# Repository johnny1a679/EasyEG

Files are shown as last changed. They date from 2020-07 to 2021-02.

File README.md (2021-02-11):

# EasyEG

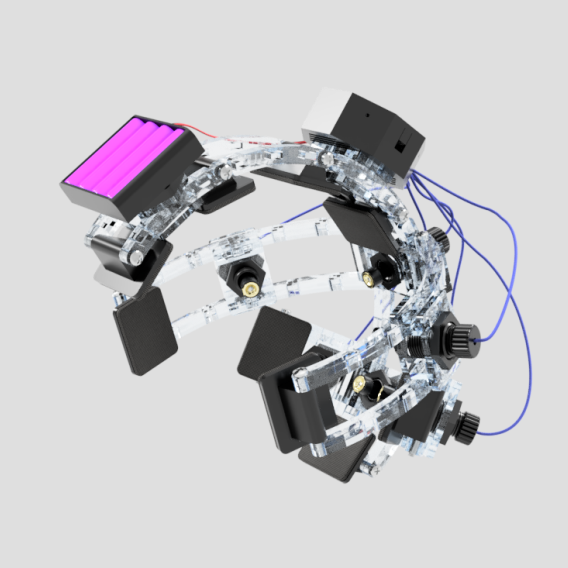
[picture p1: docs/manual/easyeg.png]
EasyEG


Brain-Computer Interfaces (BCIs) are progressively adopted by the consumer market, making them available for a variety of use-cases. However, off-the-shelf BCIs are limited in their adjustments towards individual head shapes, evaluation of scalp-electrode contact, and extension through additional sensors. This work presents __EasyEG__, a BCI headset that is adaptable to individual head shapes and offers adjustable electrode-scalp contact to improve measuring quality. __EasyEG__ consists of 3D-printed and low-cost components that can be extended by additional sensing hardware, hence expanding the application domain of current BCIs.

## Construction Manual

The following steps explain how to assemble your own __EasyEG__.
You can produce the parts either by [3D-printing](3d-printer_only) or by combining [laser cutting and 3D-printing](lasercutter_and_3d-printer) if you have access to a laser cutter and an M4 tap.

### List of Materials

#### Produced Parts With 3D-Printing Only

- 9 x [Head Plate](3d-printer_only/rails/head-plate.stl)

- [Front Rail](3d-printer_only/rails/rail_front.stl) and [Front Rail Threaded](3d-printer_only/rails/rail_front_threaded.stl)
- 2 x [Top Rail](3d-printer_only/rails/rail_top.stl) and 2 x [Top Rail Threaded](3d-printer_only/rails/rail_top_threaded.stl)
- [Long Rail](3d-printer_only/rails/rail_long.stl) and [Long Rail Threaded](3d-printer_only/rails/rail_long_threaded.stl)
- 2 x [Long Side Rail](3d-printer_only/rails/rail_side_long.stl) and 2 x [Long Side Rail Threaded](3d-printer_only/rails/rail_side_long_threaded.stl)
- 2 x [Short Side Rail](3d-printer_only/rails/rail_side_short.stl) and 2 x [Short Side Rail Threaded](3d-printer_only/rails/rail_side_short_threaded.stl)

- 2 x [Main Clamp Top](3d-printer_only/clamps/main_clamp_top.stl) and 2 x [Main Clamp Bottom](3d-printer_only/clamps/main_clamp_bottom.stl)
- 1 x [Clamp Top](3d-printer_only/clamps/clamp_top.stl) per electrode on the sides + 1 for the BCI Case
- 1 x [Clamp Bottom](3d-printer_only/clamps/clamp_bottom.stl) per electrode on the sides
- 2 x [Accessory Clamp Bottom](3d-printer_only/clamps/accessory_clamp_bottom.stl)
- 1 x [Battery Clamp Top](3d-printer_only/clamps/battery_clamp_top.stl)
- 2 x [Screw Sleeve](3d-printer_only/clamps/electrode_screwsleeve.stl)

- one of each of the following for every electrode:
  - [Electrode Nut](3d-printer_only/electrode_mount/electrode_nut.stl)
  - [Electrode Mount](3d-printer_only/electrode_mount/electrode_mount.stl)
  - [Electrode Inner Slider](3d-printer_only/electrode_mount/electrode_inner_slider.stl)
  - [Electrode Outer Screw Part 1](3d-printer_only/electrode_mount/electrode_outer_screw_part1.stl)
  - [Electrode Outer Screw Part 2](3d-printer_only/electrode_mount/electrode_outer_screw_part2.stl)

- BCI-Case [Top](3d-printer_only/bci-case_top.stl) and [Bottom](3d-printer_only/bci-case_bottom.stl)

#### Produced Parts With Laser Cutting and 3D-Printing

- Laser cut the following sheets from 4mm acrylic:
  - [Rails](lasercutter_and_3d-printer/lasercut/easyeg_lasercut_rails.svg)
  - [Clamps](lasercutter_and_3d-printer/lasercut/easyeg_lasercut_rails.svg)
- 3D-print the following:
  - 9 x [Head Plate](lasercutter_and_3d-printer/3d-prints/head-plate.stl)
  - 4 x [Main Clamp Spacer](lasercutter_and_3d-printer/3d-prints/main_clamp_spacer.stl)
  - one of each of the following for every electrode:
    - [Electrode Nut](lasercutter_and_3d-printer/3d-prints/electrode_mount/electrode_nut.stl)
    - [Electrode Screw Sleeve](lasercutter_and_3d-printer/3d-prints/electrode_mount/electrode_screwsleeve.stl)
    - [Electrode Mount](lasercutter_and_3d-printer/3d-prints/electrode_mount/electrode_mount.stl)
    - [Electrode Inner Slider](lasercutter_and_3d-printer/3d-prints/electrode_mount/electrode_inner_slider.stl)
    - [Electrode Outer Screw Part 1](lasercutter_and_3d-printer/3d-prints/electrode_mount/electrode_outer_screw_part1.stl)
    - [Electrode Outer Screw Part 2](lasercutter_and_3d-printer/3d-prints/electrode_mount/electrode_outer_screw_part2.stl)
  - BCI-Case [Top](lasercutter_and_3d-printer/3d-prints/bci-case_top.stl) and [Bottom](lasercutter_and_3d-printer/3d-prints/bci-case_bottom.stl)
  - [Battery Mount](lasercutter_and_3d-printer/3d-prints/battery_mount.stl)
  - 2 x [Electrode Nut](lasercutter_and_3d-printer/3d-prints/electrode_mount/electrode_nut.stl) for case and battery pack
  - 2 x [Electrode Screwcollet](lasercutter_and_3d-printer/3d-prints/electrode_mount/electrode_screwcollet.stl) for case and battery pack

#### External Parts
- [OpenBCI Ganglion Board](https://shop.openbci.com/products/ganglion-board?variant=13461804483) with battery pack
- [Gold Cup Electrodes](https://shop.openbci.com/collections/frontpage/products/openbci-gold-cup-electrodes?variant=9056028163)
- 1 screw - M1.6 x 6mm and 1 nut M1.6 for every electrode you want to attach
- 1 compression spring - 12mm x 35mm (thickness 0.6mm - 0.8mm) for every electrode you want to attach
- 13 screws - M4 x 50mm for assembling the rails
- 2 self-cutting countersunk screws - 3.0 x 12mm for mounting the battery pack
- 4 self-cutting flathead screws - 3.0 x 6.5mm for closing the BCI case
- foam or soft fabric to cushion the head plates

### Assemble the Rails
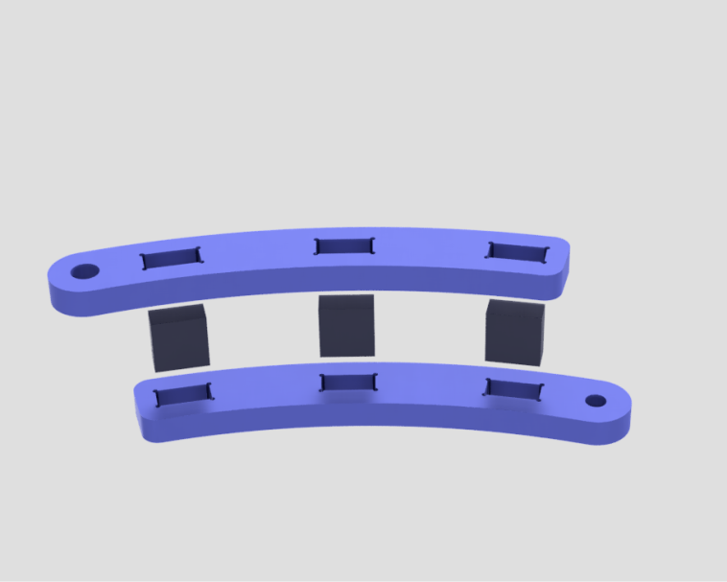
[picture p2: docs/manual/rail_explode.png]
Rail assembly


To assemble a rail take the two parts of the rail and connect them with the rectangular dowels.
They should have a good pressure fit and don't need glue.

Pay attention to the direction of each rail and which side should accept the screws.
This will later determine from which side you adjust the rails.



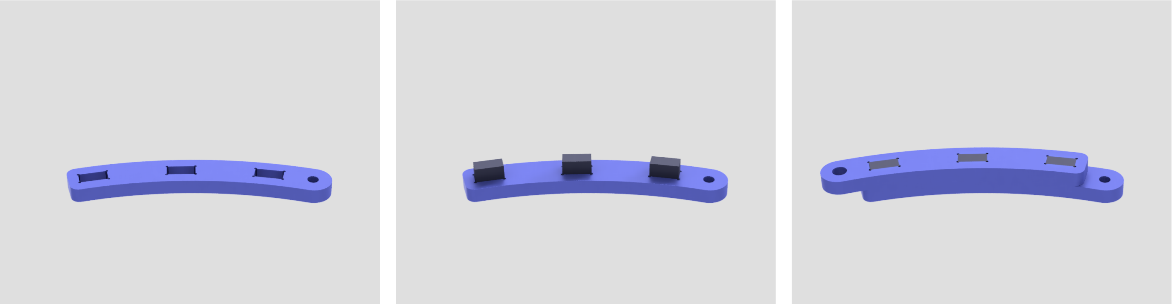
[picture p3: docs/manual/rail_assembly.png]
Rail assembly


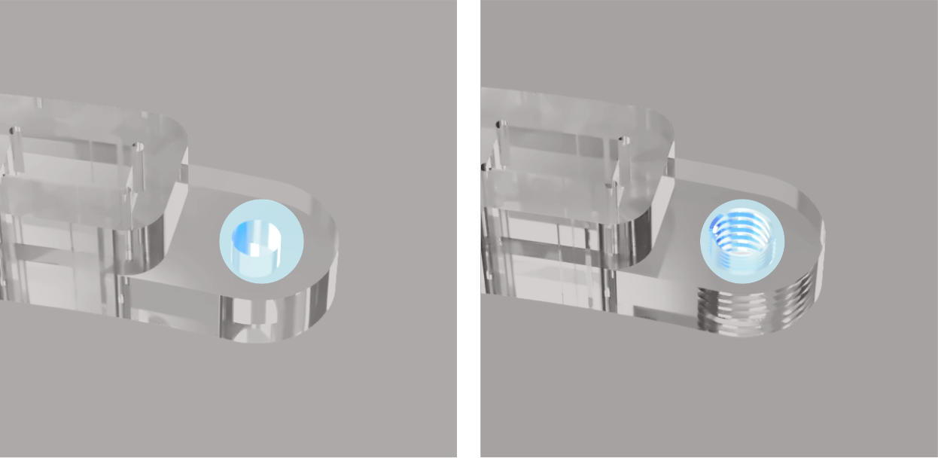
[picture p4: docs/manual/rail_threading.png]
Tapping


The rails have two sizes of holes on their ends.
The smaller holes have to be tapped with an M4 tap to later accept the screws.


### Assemble the Clamps

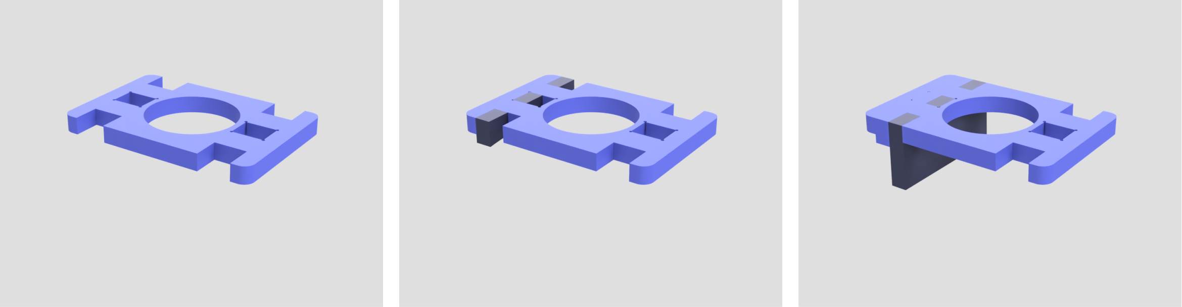
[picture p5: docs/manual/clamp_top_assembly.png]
Clamp Assembly Top


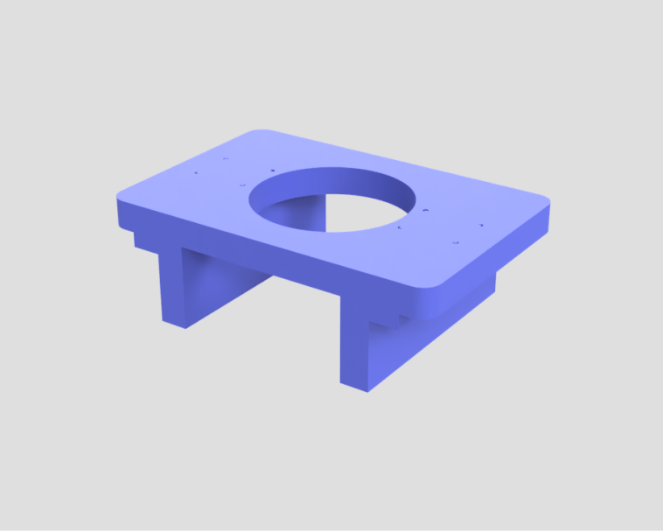
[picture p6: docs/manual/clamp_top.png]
Clamp Top


The clamps have each an upper and a lower half and will hold the electrodes.
To assemble the upper half insert the concave brakes and the guiding plates in the top Plate.



The lower half takes the convex brakes.
Again, it should be a good pressure fit.

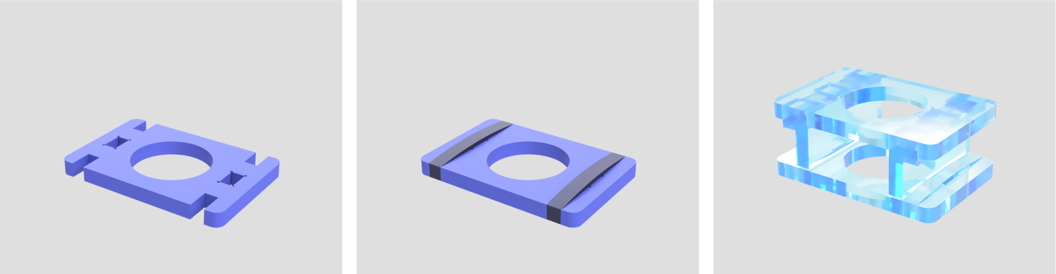
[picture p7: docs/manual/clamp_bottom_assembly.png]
Clamp Assembly Bottom


The main clamps (bigger top and bottom plate without rounded corners) take an electrode and will connect the side rails with the center rails.
They are built in the same way as the normal Clamps but take additional four pieces on the sides to later hold the side rails.

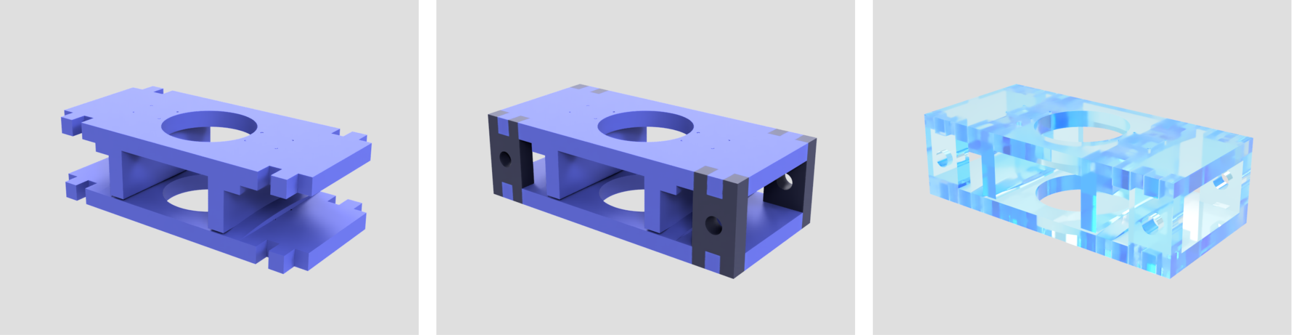
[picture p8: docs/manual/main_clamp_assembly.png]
Main Clamp Assembly


### 3D-Printed Alternatives

If you 3D-printed everything the rails and halves of the clamps are already assembled and tapped.
The orientation of the printed rails is planned to later accept screws from the right.
If you want to change this, mirror the rails before printing.

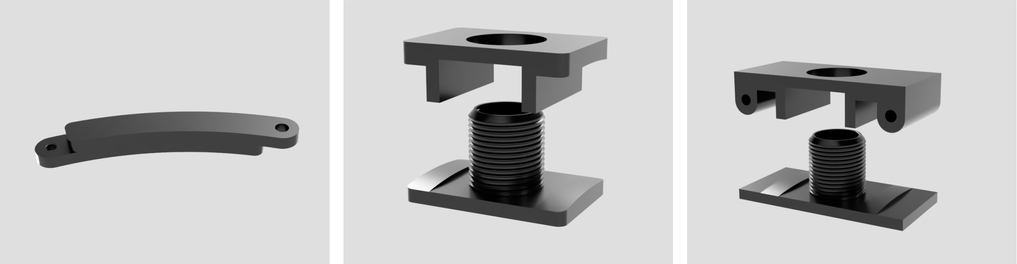
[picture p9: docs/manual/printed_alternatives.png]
3D-Printed Alternatives


### Electrode Mounts

The electrodes are screwed to the small piece of the electrode mounts (M1.6 screw and nut).
After screwing the electrode down, you can carefully bend the electrode shaft upwards to later fit the slider of the mount.

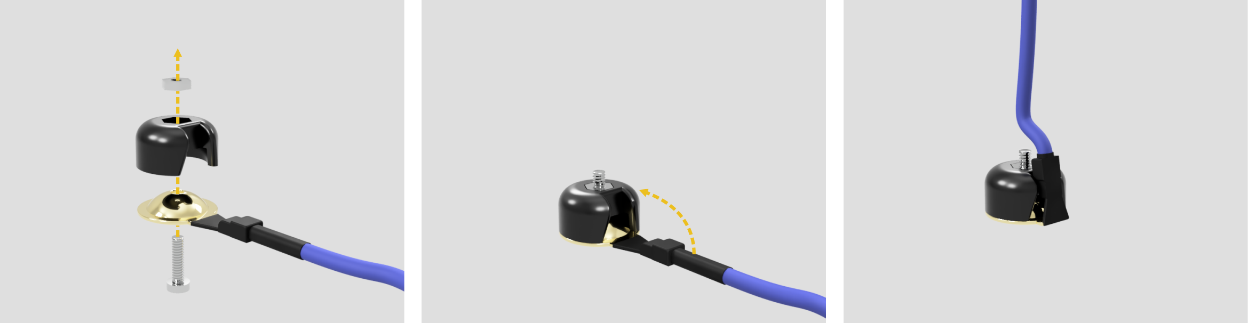
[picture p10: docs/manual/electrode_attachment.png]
Electrode Attachment


Thread the electrode wire through the slider and the spring.
Then push the screwed down electrode in the lower end of the slider.
Depending on your 3D-printer and print settings this connection might stay in place by a pressure fit or otherwise needs a drip of glue to become stable.
There is a recess to accept the shaft of the electrode.
To finish the mount surround the slider and the spring with the two halves of the outer screw.
It is no problem if the halves don't stay in place on their own as they will be held together later by the screw sleeve.

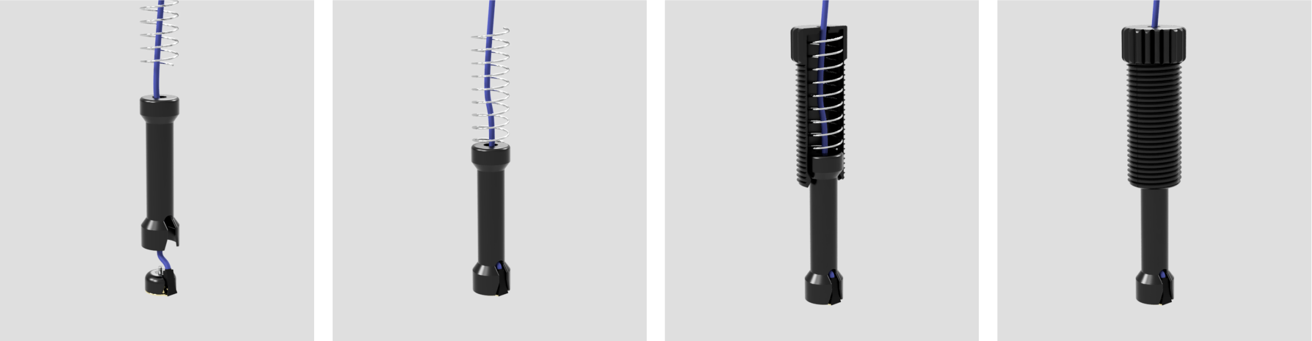
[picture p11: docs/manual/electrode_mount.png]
Electrode Mount


### Assemble Accessory Mounts
The battery pack to power the BCI is mounted on a special clamp.
It is built the same way as the normal clamps but has a peak with a hole on each side.
To mount the battery pack, it is screwed down on the 3D-printed battery mount plate (self-cutting countersunk screws).
The screws should also extend to the battery mount clamp.
This way the plate and the clamp are joined by the screws and later by the screw sleeve from below.
(In the 3D-printed version the mount plate and the cplamp top are allready one piece.)

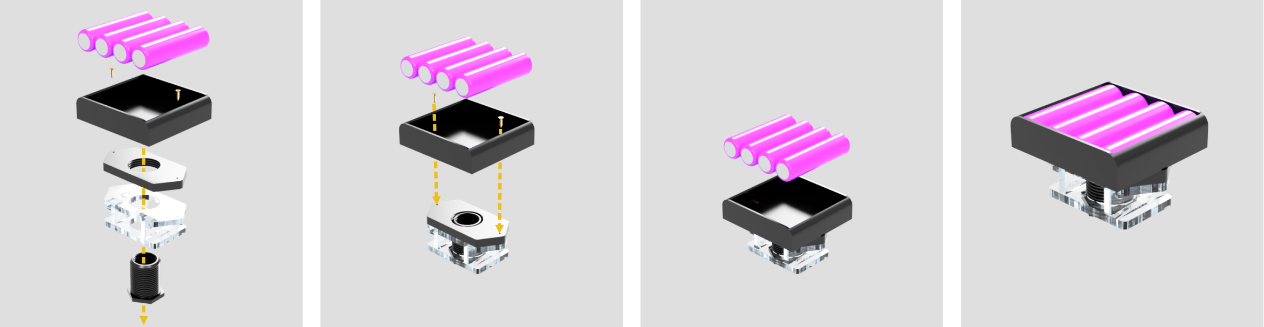
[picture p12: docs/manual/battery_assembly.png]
Battery Pack


The Case for the BCI module consists of two parts (top and bottom).
Place the plastic feet of the module in the recesses of the case.
The closed Case can be screwed together with four screws from the sides (self-cutting flathead screws).
Later the case will be fixed to one of the clamps by using one of the screw sleeves.

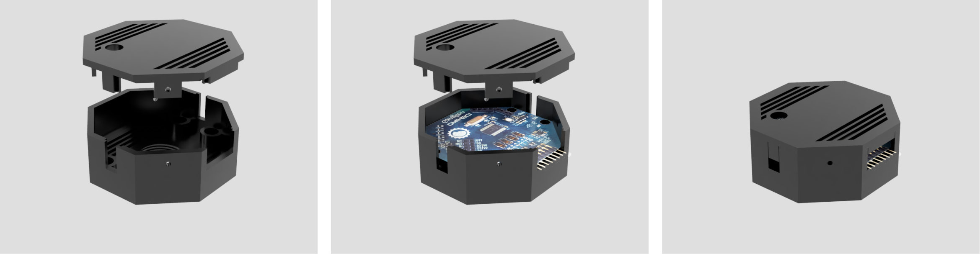
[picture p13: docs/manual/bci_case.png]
BCI Case


#### 3D-Printed Versions
For the 3D-printed only versions of the accessory mounts, you need to take the accessory bottom clamp that has no integrated screw but a hole.
Instead of the missing integrated screw, use the two screw sleeves to hold the clamps together (similar to the laser cut versions).
This will later ease the positioning of the battery pack and the BCI case.

### Assemble the Helmet

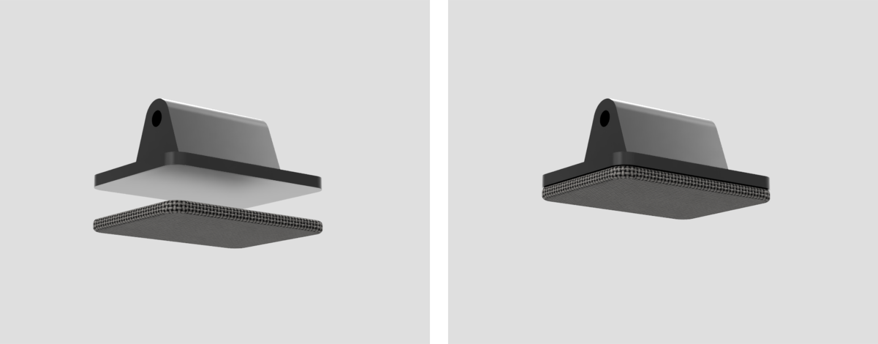
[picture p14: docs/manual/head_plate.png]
Head Plate


Before assembling the Helmet attach the foam or fabric to the head plates.



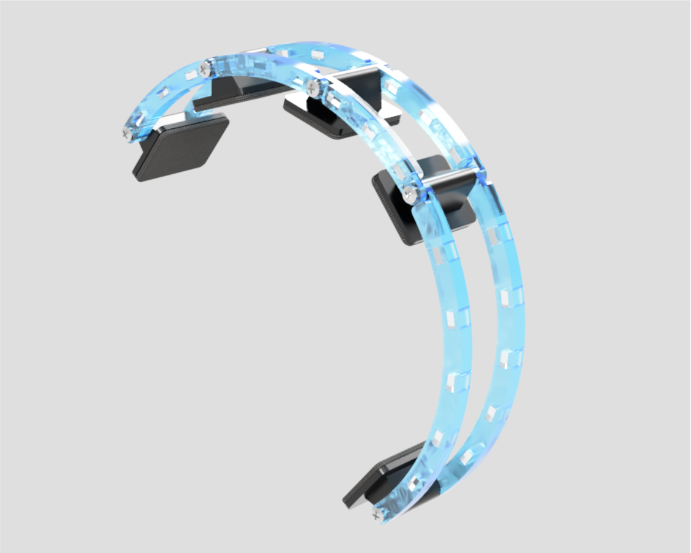
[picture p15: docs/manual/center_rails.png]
Center Rail


The center rails will be built first
There should be always two corresponding rails that are mirrored (except for the thread on one side).
They are joined with one of the M4 screws, with a head plate between the rails.
Take care, that the threaded hole is allways on the outside of the joints.
The next rails will follow the same way, while the screw also joins the new rails with the existing ones.



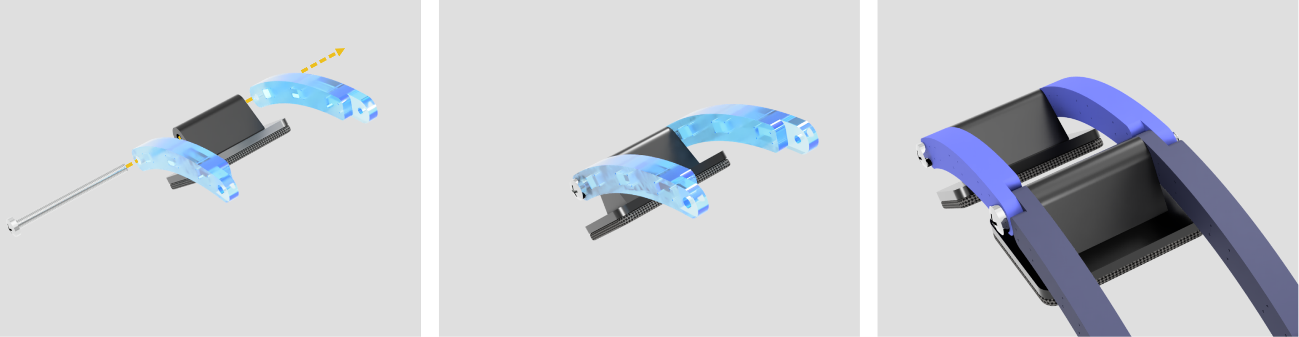
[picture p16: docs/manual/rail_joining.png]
Joining Rails


With the center rails build, the side rails can be attached.
For every side rail, one of the main clamps is taken and clamped around the center rails.
This happens by fixing them with a screw sleeve and a printed nut. (For the 3D-printed versions, only the nut is needed, as the screw sleeve is already attached.)
The electrode mounts can be inserted now or later.

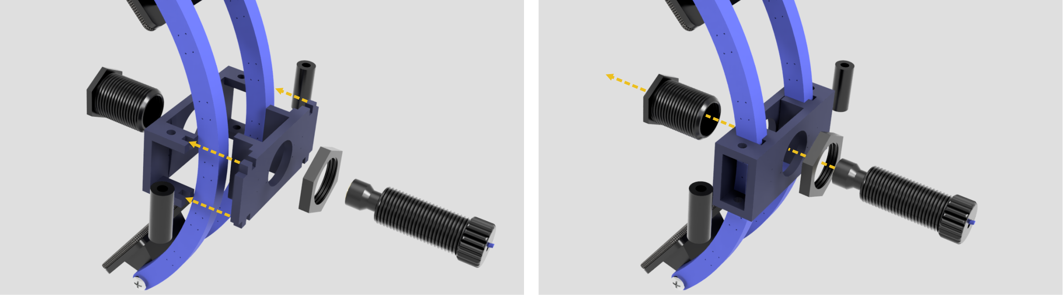
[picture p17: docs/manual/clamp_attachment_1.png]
Attaching Main Clamp


To support the side rail attachment points on the main clamps one 3D-printed spacer is inserted on each side of the clamp
(only for the laser cut version).

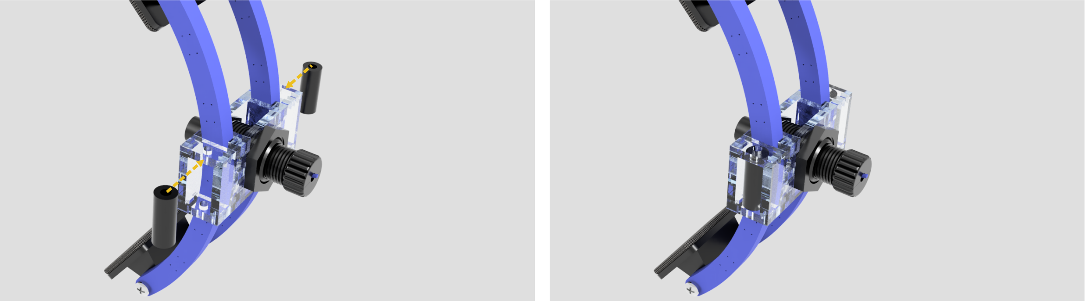
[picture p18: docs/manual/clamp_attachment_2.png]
Attaching Main Clamp


The side rails are added by screwing them (M4 Screw) through the spacer to the main clamp.
At the front of each side rail, a head plate is attached the same way as to the center rails.
Using the normal clamps, further electrodes can be attached to the side rails, in the same way as the main clamps to the center rails before.

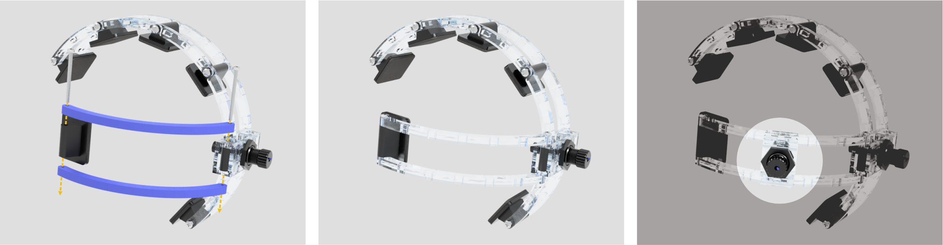
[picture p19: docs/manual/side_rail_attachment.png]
Attaching Side Rails


Following these steps, all needed electrodes and all short and long side rails can be attached.

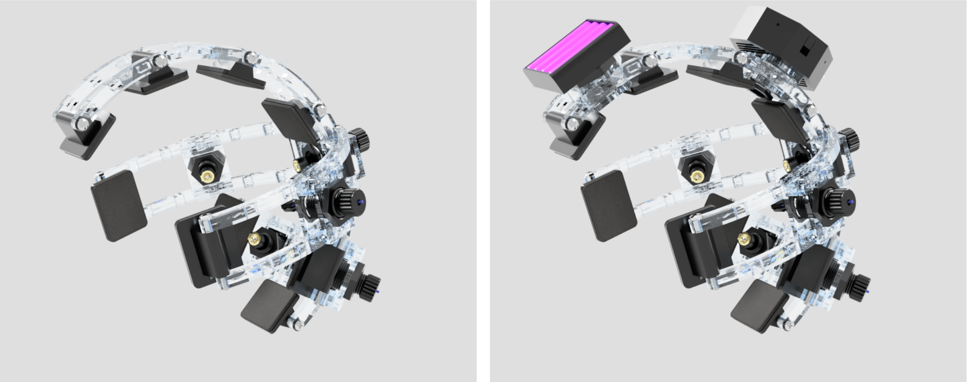
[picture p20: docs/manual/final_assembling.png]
Full Rail Assembly


After adding the BCI and battery pack (again the same way as the other clamps), all is left to do is the wiring.

### Your EasyEG Is Ready To Use!
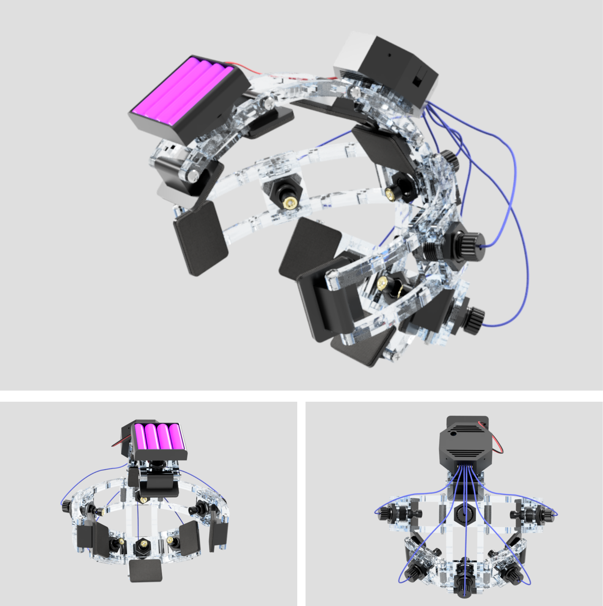
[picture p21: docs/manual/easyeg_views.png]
Fully Assembled EasyEG


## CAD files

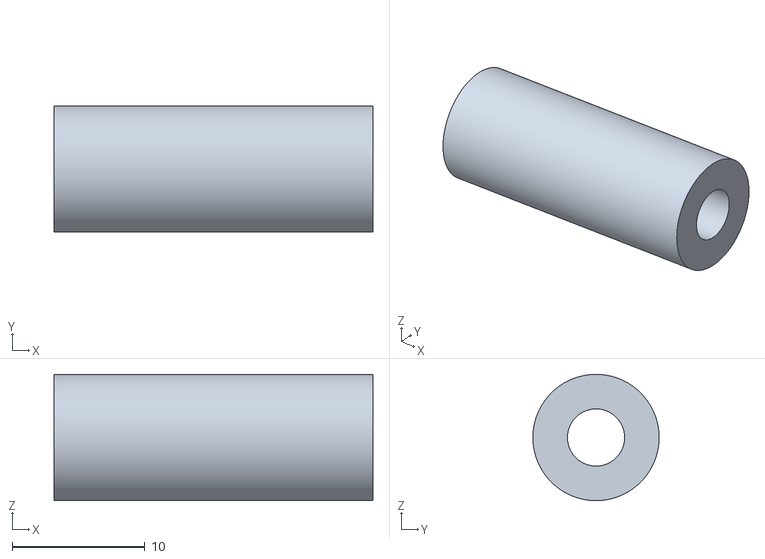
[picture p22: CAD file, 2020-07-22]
lasercutter_and_3d-printer/3d-prints/main_clamp_spacer.stl
24.0 x 9.50 x 9.50

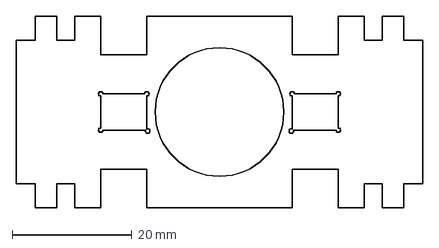
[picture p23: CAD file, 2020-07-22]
lasercutter_and_3d-printer/lasercut/clamps/main_clamp_top.dxf
68.0 x 32.0 mm

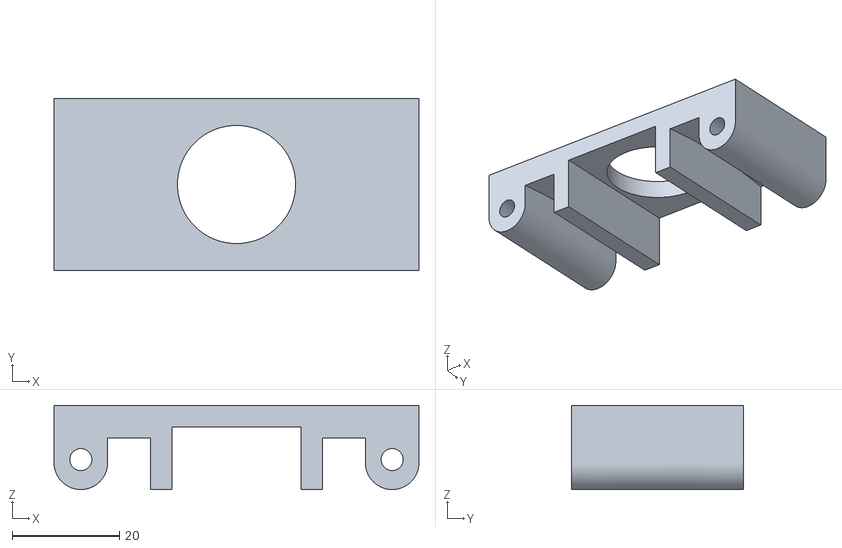
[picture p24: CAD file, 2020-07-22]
3d-printer_only/clamps/main_clamp_top.stl
68.0 x 32.0 x 15.7

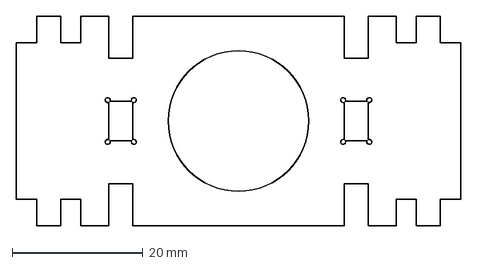
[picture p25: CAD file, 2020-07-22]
lasercutter_and_3d-printer/lasercut/clamps/main_clamp_bottom.dxf
68.0 x 32.0 mm

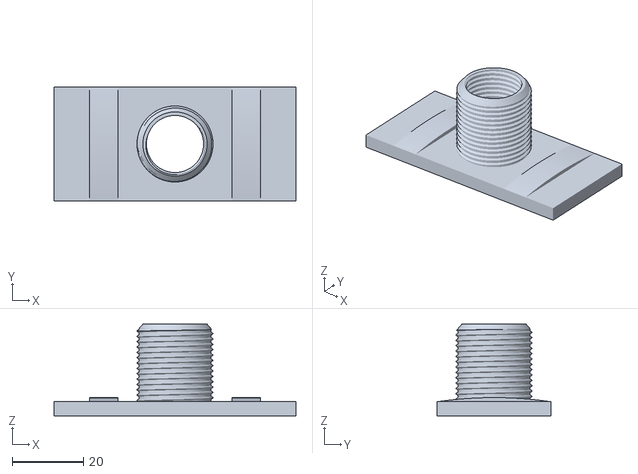
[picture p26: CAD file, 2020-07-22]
3d-printer_only/clamps/main_clamp_bottom.stl
68.0 x 32.0 x 25.8

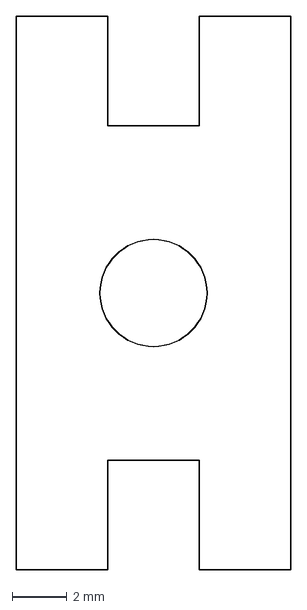
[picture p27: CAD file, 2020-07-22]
lasercutter_and_3d-printer/lasercut/clamps/main_clamp_side.dxf
10.0 x 20.2 mm

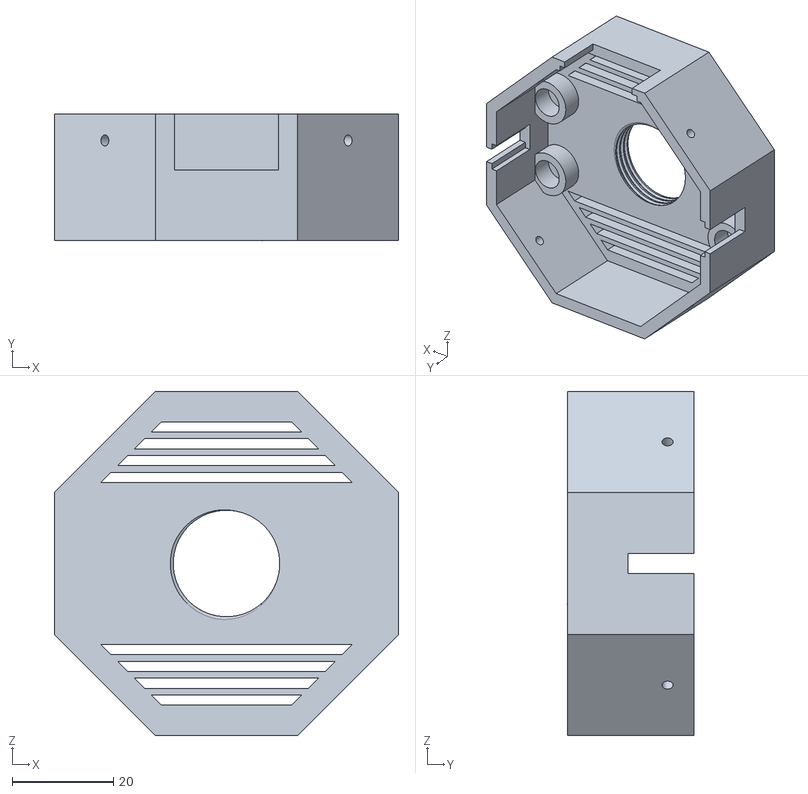
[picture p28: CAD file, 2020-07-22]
3d-printer_only/bci-case_bottom.stl
68.0 x 25.0 x 68.0

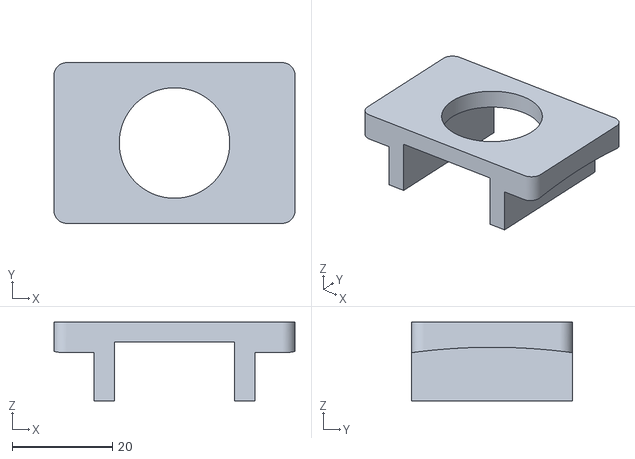
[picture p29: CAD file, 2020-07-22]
3d-printer_only/clamps/clamp_top.stl
48.0 x 32.0 x 15.7

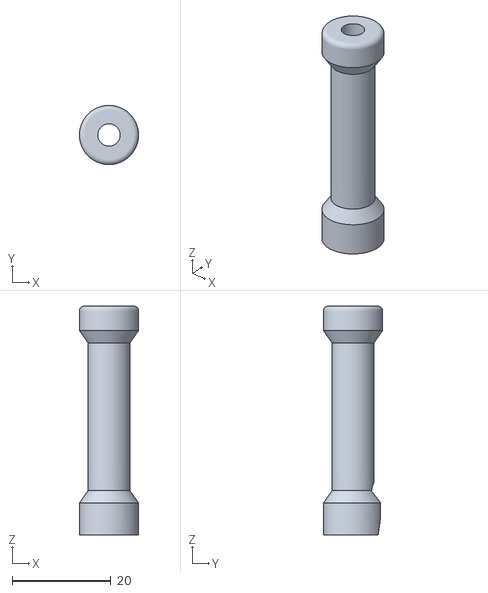
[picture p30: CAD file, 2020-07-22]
3d-printer_only/electrode_mount/electrode_inner_slider.stl
12.0 x 12.0 x 46.5

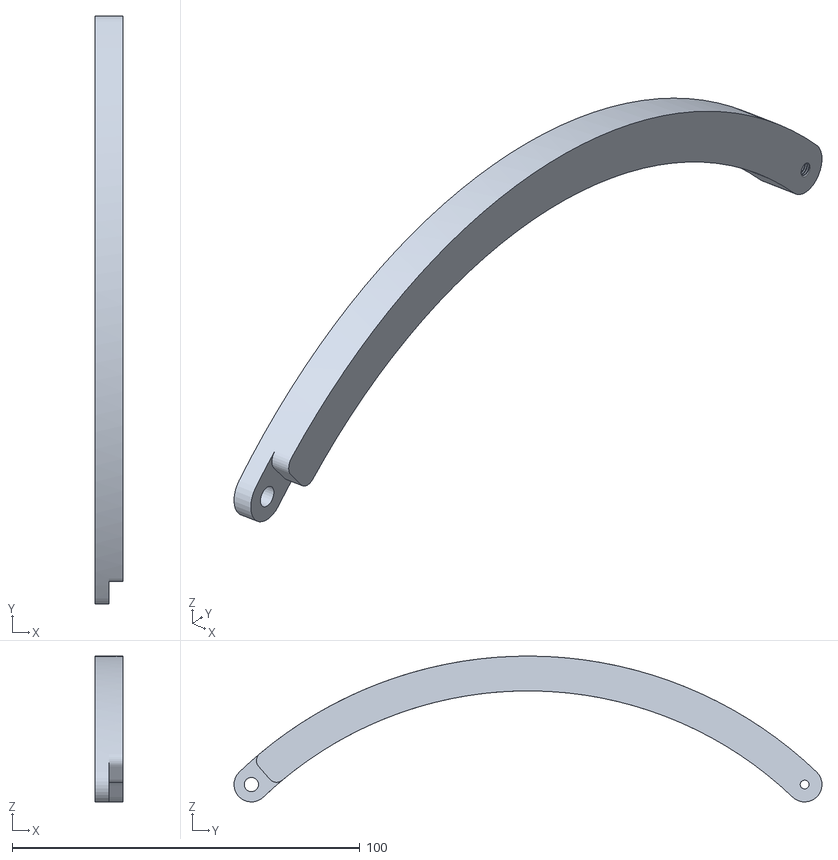
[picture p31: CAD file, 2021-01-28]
3d-printer_only/rails/rail_long_threaded.stl
8.00 x 169.0 x 41.9

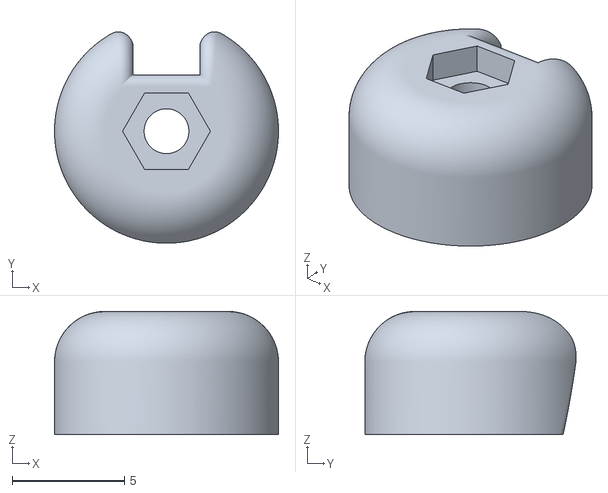
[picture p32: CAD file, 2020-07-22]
lasercutter_and_3d-printer/3d-prints/electrode_mount/electrode_mount.stl
10.00 x 9.44 x 5.50

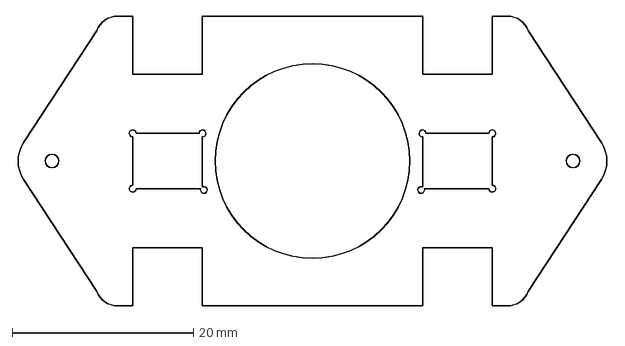
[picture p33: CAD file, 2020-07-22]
lasercutter_and_3d-printer/lasercut/clamps/clamp_battery_top.dxf
65.4 x 32.0 mm

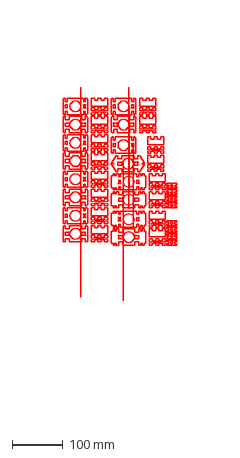
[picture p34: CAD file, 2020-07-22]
lasercutter_and_3d-printer/lasercut/easyeg_lasercut_clamps.dxf
223.7 x 791.6 mm

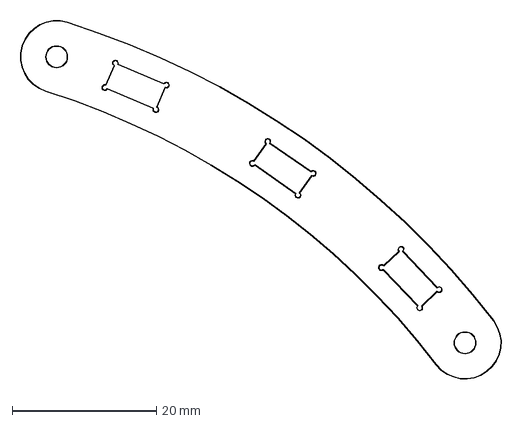
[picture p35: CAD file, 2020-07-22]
lasercutter_and_3d-printer/lasercut/rails/rail_front_outer_threaded.dxf
67.9 x 50.9 mm

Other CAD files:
3d-printer_only/bci-case_top.stl
3d-printer_only/clamps/accessory_clamp_bottom.stl
3d-printer_only/rails/head-plate.stl
3d-printer_only/clamps/battery_clamp_top.stl
3d-printer_only/electrode_mount/electrode_nut.stl
3d-printer_only/electrode_mount/electrode_outer_screw_part1.stl
3d-printer_only/electrode_mount/electrode_outer_screw_part2.stl
3d-printer_only/rails/rail_front.stl
3d-printer_only/rails/rail_front_threaded.stl
3d-printer_only/rails/rail_long.stl
3d-printer_only/rails/rail_side_long.stl
3d-printer_only/rails/rail_side_long_threaded.stl
3d-printer_only/rails/rail_side_short.stl
3d-printer_only/rails/rail_side_short_threaded.stl
3d-printer_only/rails/rail_top.stl
3d-printer_only/rails/rail_top_threaded.stl
lasercutter_and_3d-printer/3d-prints/battery_mount.stl
lasercutter_and_3d-printer/3d-prints/electrode_mount/electrode_nut.stl
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

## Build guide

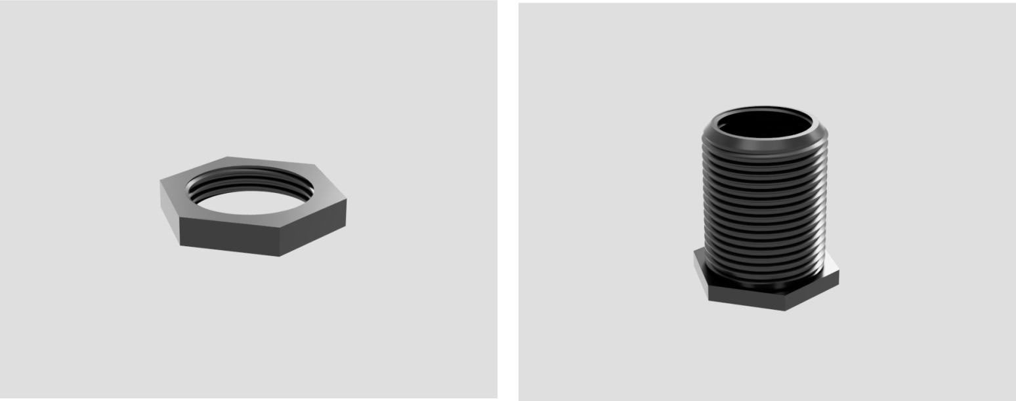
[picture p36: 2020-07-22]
docs/manual/screwing_stuff.png

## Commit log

2020-07-22 add hardware production files
    [battery_clamp_bottom.stl, battery_clamp_top.stl, battery_mount.stl, bci-case_bottom.stl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]
2020-07-22 add material list and images to the readme
    [easyeg_lasercut_clamps.dxf, easyeg_lasercut_rails.dxf]
2021-01-28 correct long threaded rail
    [rail_long_threaded.stl]
2021-02-11 copy and rename stl files for assambly rework
    [accessory_clamp_bottom.stl]
